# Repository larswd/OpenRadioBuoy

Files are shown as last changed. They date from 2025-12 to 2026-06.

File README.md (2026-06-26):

# The Open Radio Buoy (ORB)
This repository contains the firmware, list of hardware and PCB schematics that collectively make up the Open Radio Buoy (ORB), as described in our paper which you can read [here](https://arxiv.org/abs/2601.05615). The buoy is designed to be a low-cost, open-source drifter for coastal water measurements. The archive is currently incomplete, but more updates will come. 

## List of hardware components

### Drifter

A single ORB drifter's electronics is made up of the following components, with links to manufacturer website. 

| Quantity | Component | Note |
| -------- | --------- | ---- |
| 1 | [Seeed Studio Wio-E5 mini](https://wiki.seeedstudio.com/LoRa_E5_mini/) | Comes with actory protection which needs to be disabled manually |
| 1 | [Adafruit Ultimate GPS](https://www.adafruit.com/product/746)          | Comes with a holder for a CR1220 clock battery to remember last fix.| 
| 1 | [Adafruit SD Breakout](https://www.adafruit.com/product/254)           | | 
| 1 | [DS18B20 temperature sensor](https://www.sparkfun.com/temperature-sensor-waterproof-ds18b20.html) | |
| 1 | [Pololu 3.3 V Step up/Step down voltage regulator](https://www.pololu.com/product/2122) | |
| 1 | 10 kOhm resistor  |
| 1 | 4.7 kOhm resistor  |
| 2 | 33.0 Ohm resistors |
| 1 | Magnetic switch         | Normally open is *strongly* recommended. Not mandatory. |
| 1 | [CAB-14574 connector](https://no.mouser.com/ProductDetail/474-CAB-14574) | Not mandatory, but makes arming and disarming the drifter easier |
| 1 | Strong magnet | To turn off the buoy from outside the buoy container | Not mandatory |

As for battery power, the buoy works with any kind of power source with a voltage between 2.7 and 11.8 V, as per the Pololu documentation. This can be either a Lithium battery such as [Saft LSH20](https://www.nkon.nl/novat/saft-lsh-20-lithium-battery-3-6v.html), although any user should be aware of the [risks of using Lithium powered batteries](https://www.relionbattery.com/blog/the-truth-about-lithium-batteries-and-safety). Alternatively, several alkaline batteries (as was done by the [SFY](https://github.com/gauteh/sfy)) in series can be utilised without need of modifying the circuit. 

### Base station

A single ORB base station electronics is made up of the following components, with links to manufacturer website. 

| Quantity | Component | Note |
| -------- | --------- | ---- |
| 1 | [Seeed Studio Wio-E5 mini](https://wiki.seeedstudio.com/LoRa_E5_mini/) | Comes with actory protection which needs to be disabled manually |
| 1 | [Adafruit SD Breakout](https://www.adafruit.com/product/254)           | Not mandatory |
| 1 | [Pololu 5 V Step up/Step down voltage regulator](https://www.pololu.com/product/4082) | |
| 1 | [CAB-14574 connector](https://no.mouser.com/ProductDetail/474-CAB-14574) | Not mandatory, but makes arming and disarming the drifter easier |
| 1 | [Blues Notecard Cellular](https://shop.blues.com/collections/notecard/products/notecard-cellular?variant=44541263118577) | Check the coverage diagram for your area before ordering |
| 1 | [Blues Notecarrier A](https://shop.blues.com/products/carr-al) | |
| 1-2 | Capacitor (One [1F](https://no.mouser.com/ProductDetail/Eaton-Electronics/KVR-5R0V105-R?qs=4ASt3YYao0XQhknEZPCgzw%3D%3D) or two [10F](https://no.mouser.com/ProductDetail/Knowles-Illinois-Capacitor/DGH106Q2R7C?qs=vmHwEFxEFR9tIw5tsmf9eg%3D%3D)) | Capacitor strength dependent on power source |

If you choose to power the base station with Lithium batteries like the aforementioned LSH20, then a single 1 F capacitor is sufficient to keep the base station operational. If, however, you use alkaline batteries as your power source then 10 F capacitors are required to ensure that the high energy spikes drawn by the GSM module can be met. 

### Other components
To code the WiO E5 mini, remember to order at least one [ST link](https://www.adafruit.com/product/2548) and some [Female-Male jumper cables](https://no.rs-online.com/web/p/breadboard-jumper-wires/2048242) in order to be able to upload the software to the buoys and base stations. 

## Assembly instructions

### Electronics assembly - Buoys
Order the [PCBs](https://github.com/larswd/OpenRadioBuoy/tree/main/hardware/buoy_PCB) by uploading the Gerber files folder to your favourite PCB manufacturer, such as [JLCPCB](https://cart.jlcpcb.com/quote?spm=jlcpcb.Public.2006) or [Seeed studio](https://www.seeedstudio.com/fusion_pcb.html). Then order the components listed above according to how many buoys you plan to make. They can be ordered either from the manufacturer, and in many cases from a local electronics distributor. 

The assembly can begin once you have all the components at hand. The PCBs offered are currently Through-Hole PCBs, and requires therefore manual soldering. As both sides of the PCB is utilized in somewhat overlapping segments, it is vital that some components are soldered before others. I would recommend soldering in this order: 

1. Wires to the power pins at the bottom of the PCB
2. Pololu
3. Trim the pins on the back of the Pololu, then tape. 
4. SD card writer
5. Trim the pins on the back of the SD card writer, then tape.
6. GPS
7. Trim GPS pins
8. Wio E5 mini
9. MF pin sockets for the programmable pins
10. DS18B20
11. Resistors
12. Magnetic switch
13. Battery connectors
    
### Electronics assembly - Base stations
Order the [PCBs](https://github.com/larswd/OpenRadioBuoy/tree/main/hardware/BST_PCB) by uploading the Gerber files folder to your favourite PCB manufacturer, such as [JLCPCB](https://cart.jlcpcb.com/quote?spm=jlcpcb.Public.2006) or [Seeed studio](https://www.seeedstudio.com/fusion_pcb.html). Then order components according to the amount of base stations you plan on creating. 
The assembly can begin once you have all the components at hand. The PCBs offered are currently Through-Hole PCBs, and requires therefore manual soldering. Unlike the buoy PCBs, there is little overlap between components and they can be soldered on in pretty much any order. Some things to keep in mind

1. The power regulator will somewhat block easy access to the USB port on the LoRa module. Hence, it is strongly recommended to not solder the module directly onto the board. Instead, we recommend soldering on a 1x5 2.54 mm MF pin header, as the power regulator then easily can be removed and reattached if you need to upload software updates. 
2. Super capacitors have a polarity, indicated by the arrows on both the PCB and often on the capacitors themselves. Please check the data sheet of your capacitor before soldering. 
3. The Notecard might need to be initialized before use. A handy guide can be found [here](https://dev.blues.io/quickstart/notecard-quickstart/notecard-and-notecarrier-a/).
4. The notecard sends the data to Blues' Notehub, which is project based. By default, the ORB base station is set to send the data to a notehub project owned by us. We are willing to share any data we receive as well as the url to our dashboard, but if you want to administrate your data yourself, and who gets access to it, then you can create your own project at [https://notehub.io/projects], then you simply exchange the notehub project url at (currently) line 14 in [the GSM module header](https://github.com/larswd/OpenRadioBuoy/tree/main/firmware/common_libraries/gsm/src/gsm.h) with your new project url (which should look something like ```me.proton.larswd:my_cool_project```)

### Installation instructions - Buoy
The installation of the ORB firmware is a two-step process. First, you need to remove the write protection that the WiO-E5-mini comes with out of the box. To do so, you first need a USB C cable and a [ST-Link](https://www.adafruit.com/product/2548). Then, download the [STM32CubeProgrammer](https://www.st.com/en/development-tools/stm32cubeprog.html#get-software), and install it. Once it is installed, connect the Wio-E5 mini to your laptop via both the USB C cable and with the ST-link. Here, you need to connect the right pins, and we list them as (ST Link pin/Wio pin), 
- (RST/RST),
- (SWCLK/CLK),
- (SWDIO/DIO),
- (GND/GND).
Afterwards, set ```shared``` to ```Enabled``` and ```Reset mode``` to ```Hardware reset```. If you press the circular arrows button, then if everything works you should see under the **OB** header an option called **Read out protection**, set this drop-down menu to AA and press **Apply**. The buoy is now programmable! See a helpful visual guide below: 

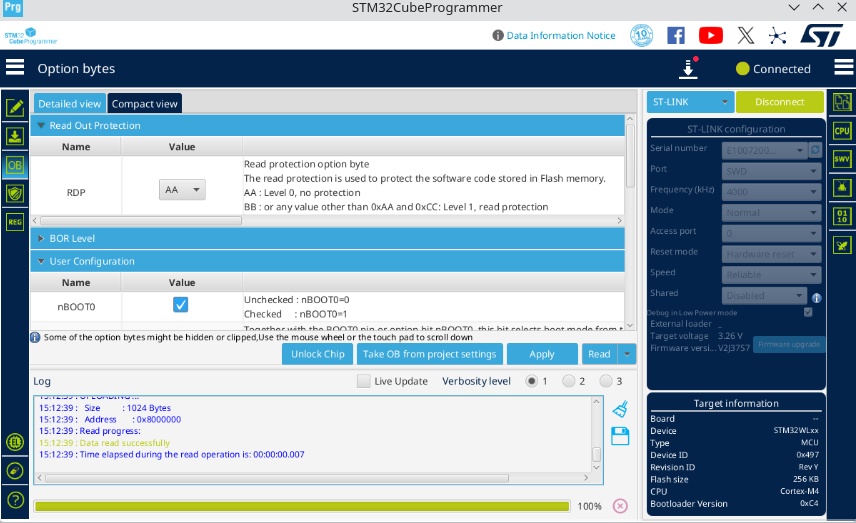
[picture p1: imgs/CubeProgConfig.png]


The next step is to upload the firmware. If you are happy with the default configuration, then you can jump to the next paragraph. Otherwise, you can configure most important parameters in the [configuration file](firmware/drifter/src/config.h). What each parameter does is described in the [drifter README file](firmware/drifter/README.md).

Once you have a configuration file you are satisfied with, you can upload the firmware to the buoy. To do so, we use [PlatformIO IDE for vscode](https://docs.platformio.org/en/latest/integration/ide/vscode.html), an extension for visual studio code made for programming microcontrollers. Once you have installed platformIO, click **Open project** under the **PIO Home** tab, and navigate to the *firmware/drifter* folder and click **Open drifter**. From here, platformio will open and read the necessary configurations. Once the project has finished loading, which you can see when several new buttons have appeared at the bottom taskbar in visual studio code, then you can upload the code. An image of a fully loaded platformio instance is shown below, in particular note the checkmark and arrow key at the very bottom. 
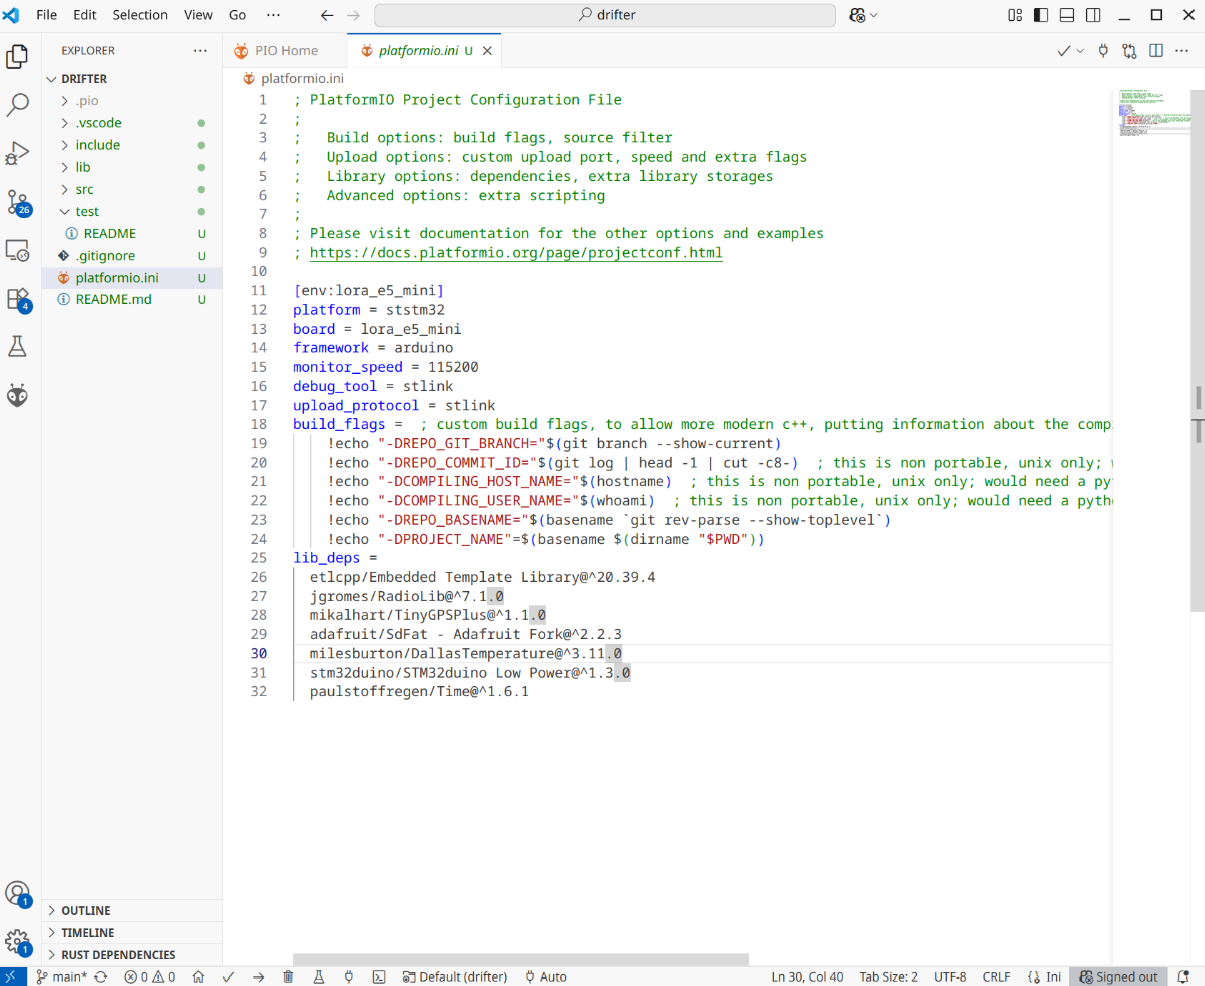
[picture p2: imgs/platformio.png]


To upload the code, connect the ORB to your computer both with the ST link (connection instructions are given above) and the USB C cable, then press the upload button (The arrow icon), then wait until the terminal that popped up states something close to 
```
============================================= [SUCCESS] Took 3.12 seconds =============================================
```
### Installation instructions - Base station
The steps for installing the firmware to the base station is more or less the same as the buoy one, with the exception that you instead open the **basestation** project rather than the **drifter** project. Furthermore, you should here remember to go into the ```config.h``` file and set a unique base station ID. See the line where it says:
static constexpr uint8_t base_station_ID            {x};```
Where ```x``` is some number. Set ```x``` to any whole number between 0 and 255 that you have not previously used in your base station fleet, then upload the code to the base station. **REMEMBER**: See bullet point 4 of the assembly instructions for the base station regarding data management. 

### Final assembly 

The container components we used are given in the table below 

| Component | Role |
| --------- | ---- |
| [Pipe connector](https://www.biltema.no/bygg/vvs/sanitet-og-vann/avlop/innendors-avlop-gra/innendors-avlop-gra-75-mm/avlopsror-skjotemuffe-75-mm-2000059003) | Main electrical component housing |
| [Lid 75 mm](https://www.biltema.no/bygg/vvs/sanitet-og-vann/avlop/innendors-avlop-gra/innendors-avlop-gra-75-mm/avlopsror-endestopp-75-mm-2000059011) | Top lid |
| [Reduction 75->50mm](https://www.biltema.no/bygg/vvs/sanitet-og-vann/avlop/innendors-avlop-gra/innendors-avlop-gra-75-mm/avlopsror-reduksjon-o-7550-mm-2000065100) | Ballast and battery container |
|[Lid 50 mm](https://www.biltema.no/bygg/vvs/sanitet-og-vann/avlop/innendors-avlop-gra/innendors-avlop-gra-50-mm/avlopsror-endestopp-o-50-mm-2000065102) | Bottom lid |
| [Large cable gland](https://no.rs-online.com/web/p/cable-glands/6694673) | Cable gland for the antenna |
| [Small cable gland](https://no.rs-online.com/web/p/cable-glands/6694660) | Cable gland for DS18B20 |
| [Ballast](https://www.frederiksen-scientific.no/produkt/lodd-med-krok-200-g/191002) | We use 300 grams of tin ballast in each ORB drifter |
| [XPS 300](https://thaugland.no/butikk/byggevarer/isolasjon/mark-grunn-isolasjon/xps/jackon-isolasjon-xps-20mm-300-jackofoam/) | 20 mm isolation foam as a flotation device around the top for increased stability. |

To assemble, drill two holes in the top lid for the two cable glands. Thereafter, sand the lid to ensure that the top is as uniform as possible. Apply generously with grease on each of the rubber bands on the cable glands and inside the pipes. Insert the fully assembled ORB electronics through the cable glands in the lid. Tighten the antenna gland, but not the thermistor gland, and watch carefully to ensure that the tightening does not loosen the antenna connection to the main circuit board. Insert the bottom lid into the reduction, then place the ballast in the bottom 50 mm diameter pipe, use silicone or other lipophile glue to ensure that it stays put, and add a small cardboard or plastic disc at the top to ensure an even surface. Mark where the magnetic switch is supposed to be placed on the pipe connector with permanent marker, then tape the switch on the other side underneath the marker. Be careful, as improper switch placement means that it is difficult to check if the buoy is turned off while inactive. Cut out a small square or disk of the XPS 300, approximately 15 cm wide at the widest, and cut a 75 mm diameter hole in the middle. Insert the lid into the XPS 300, and then into the pipe connector. Connect the battery to the electronics, and validate that the switch works as intended. Finally, insert the reduction into the connector, and seal the buoy by tightening the thermistor cable gland. 


Your ORB drifter is now ready to use. 

### Final assembly - Base station

As the base stations will, most likely, not be floating in water directly, there is significantly more leeway in container design. Pick any waterproof container large enough, and drill a single hole large enough for the [cable gland](https://no.rs-online.com/web/p/cable-glands/6694673). In our deployments, we used this [fishing box](https://www.clasohlson.com/no/Vanntett-boks-/p/31-8544) which could fit three D Cell batteries and the base station, although it was a bit too cramped. Hence, we recommend finding a slightly larger container if possible. 

## Images and deployments
Images from the deployments will come soon. 

## A small thanks 
We would also like to thank the authors of the many open source libraries that collectively form the code base of the Open Radio Buoy. In no particular order, we wish to express our gratitude to 
- [Paul Stoffregen and contributors' OneWire](https://github.com/PaulStoffregen/OneWire)
- [Mikal Hart and contributors' TinyGPSplus](https://github.com/mikalhart/TinyGPSPlus)
- [Jan Gromeš and contributors's Radiolib](https://github.com/jgromes/RadioLib)
- [Bill Greiman's SdFat](https://github.com/greiman/SdFat)
- [Jean Rabault's OpenMetBuoy](https://github.com/jerabaul29/OpenMetBuoy-v2021a)

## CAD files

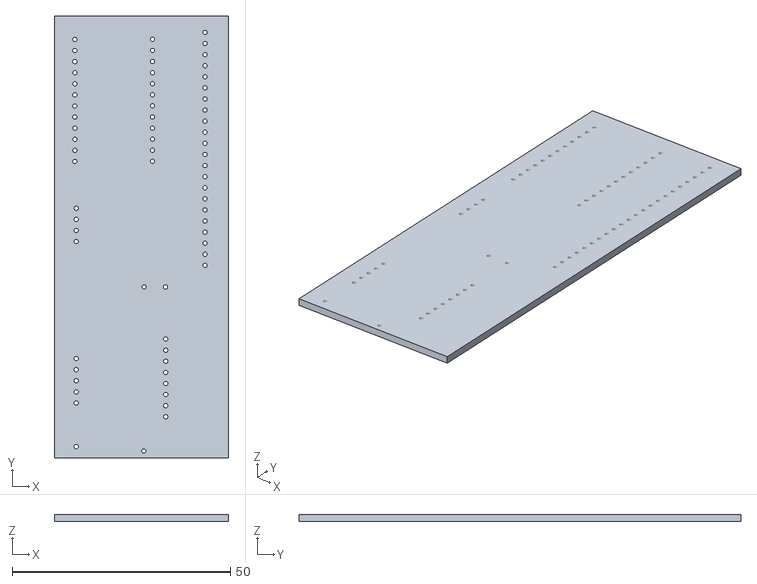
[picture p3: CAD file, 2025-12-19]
hardware/BST_PCB/BST_BCP.stl
39.9 x 101.2 x 1.60

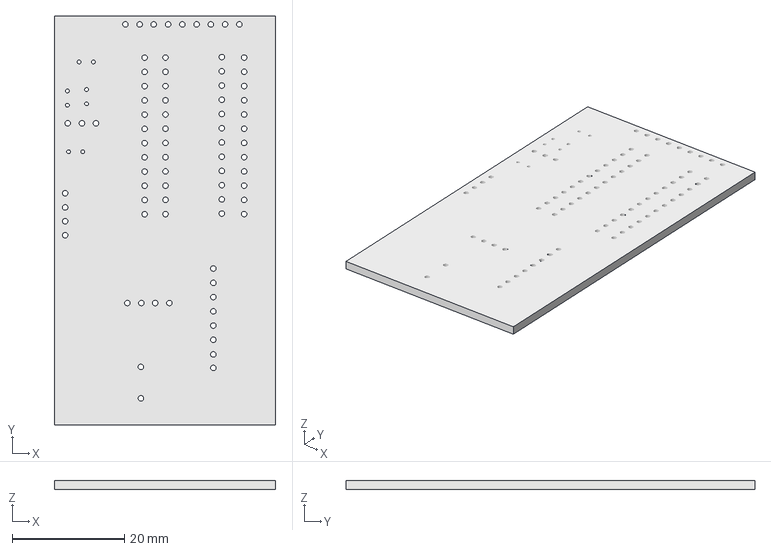
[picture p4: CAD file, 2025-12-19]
hardware/buoy_PCB/PCB_FCAD.FCStd
39.5 x 73.0 x 1.60 mm
Pcb_11bb
Pcb_11bb (Meshed)

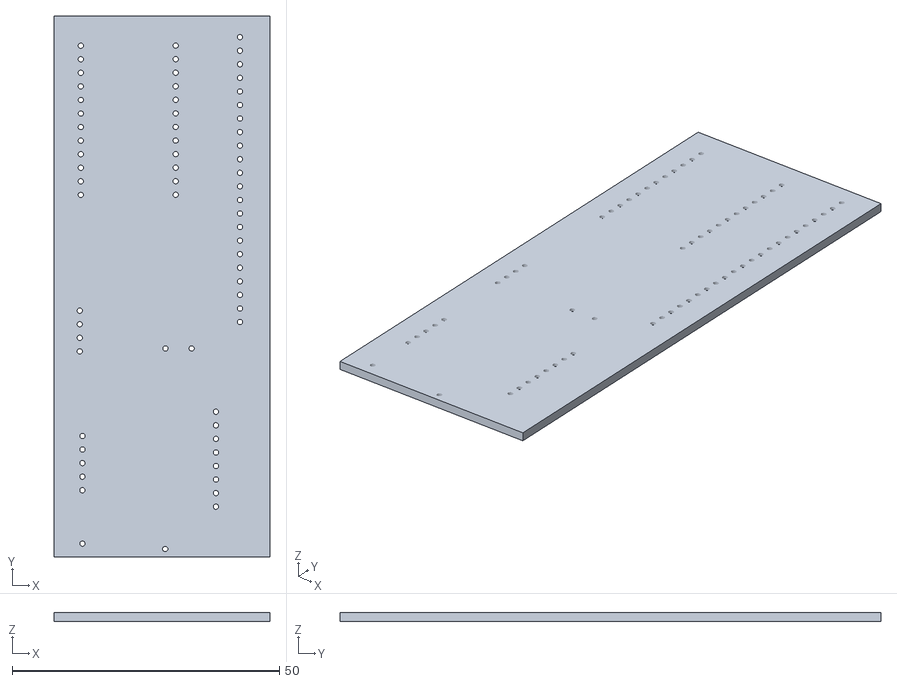
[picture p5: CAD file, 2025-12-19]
hardware/BST_PCB/BST_BCP_v2.stl
40.4 x 101.3 x 1.60

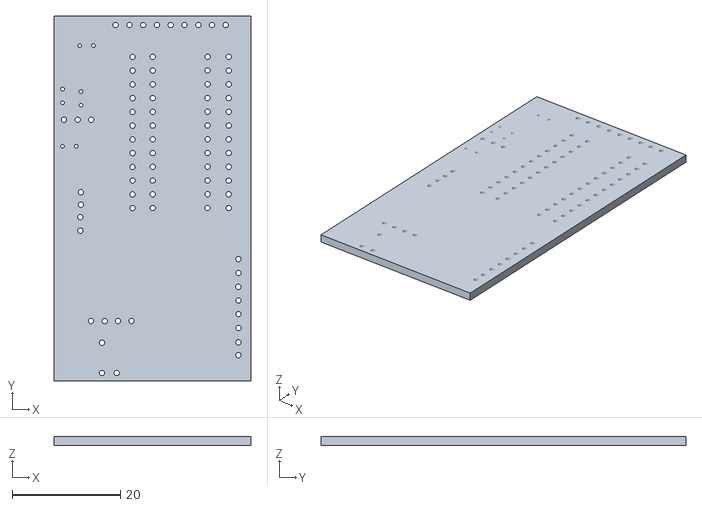
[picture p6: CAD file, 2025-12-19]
hardware/buoy_PCB/PCB_meshed.stl
36.4 x 67.4 x 1.60

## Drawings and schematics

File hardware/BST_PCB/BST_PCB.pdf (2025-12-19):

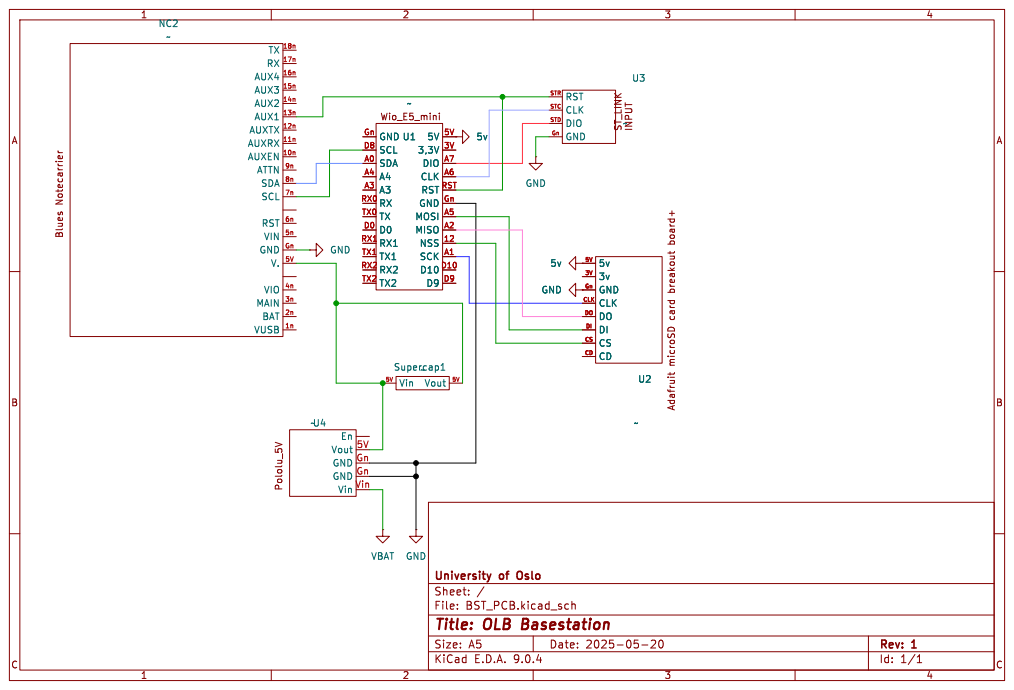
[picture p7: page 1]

Id: 1/1 Title: OLB Basestation

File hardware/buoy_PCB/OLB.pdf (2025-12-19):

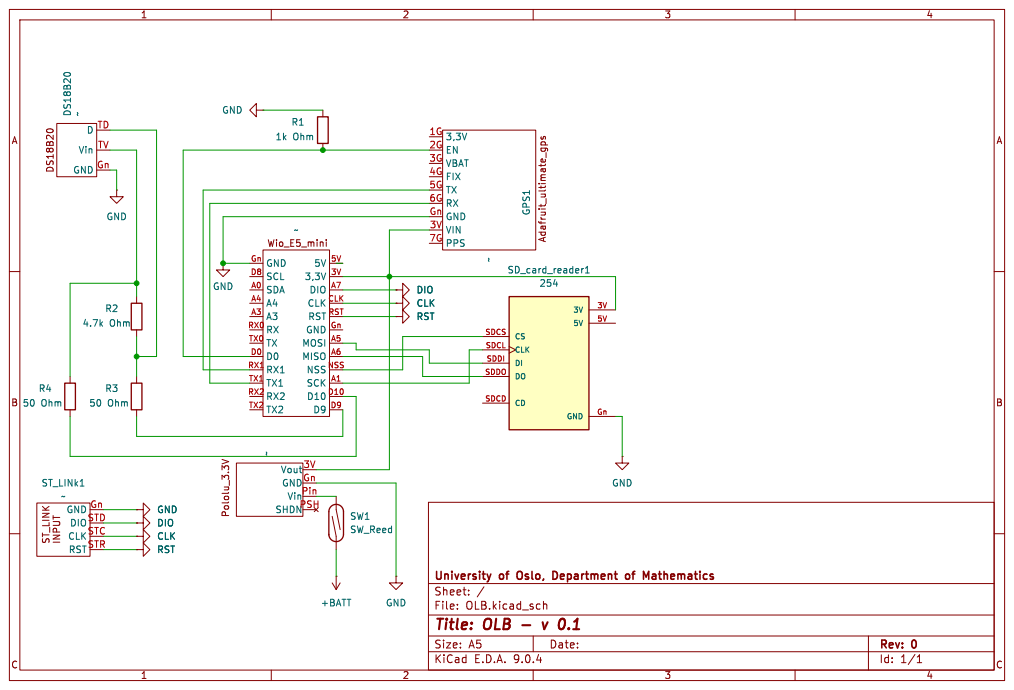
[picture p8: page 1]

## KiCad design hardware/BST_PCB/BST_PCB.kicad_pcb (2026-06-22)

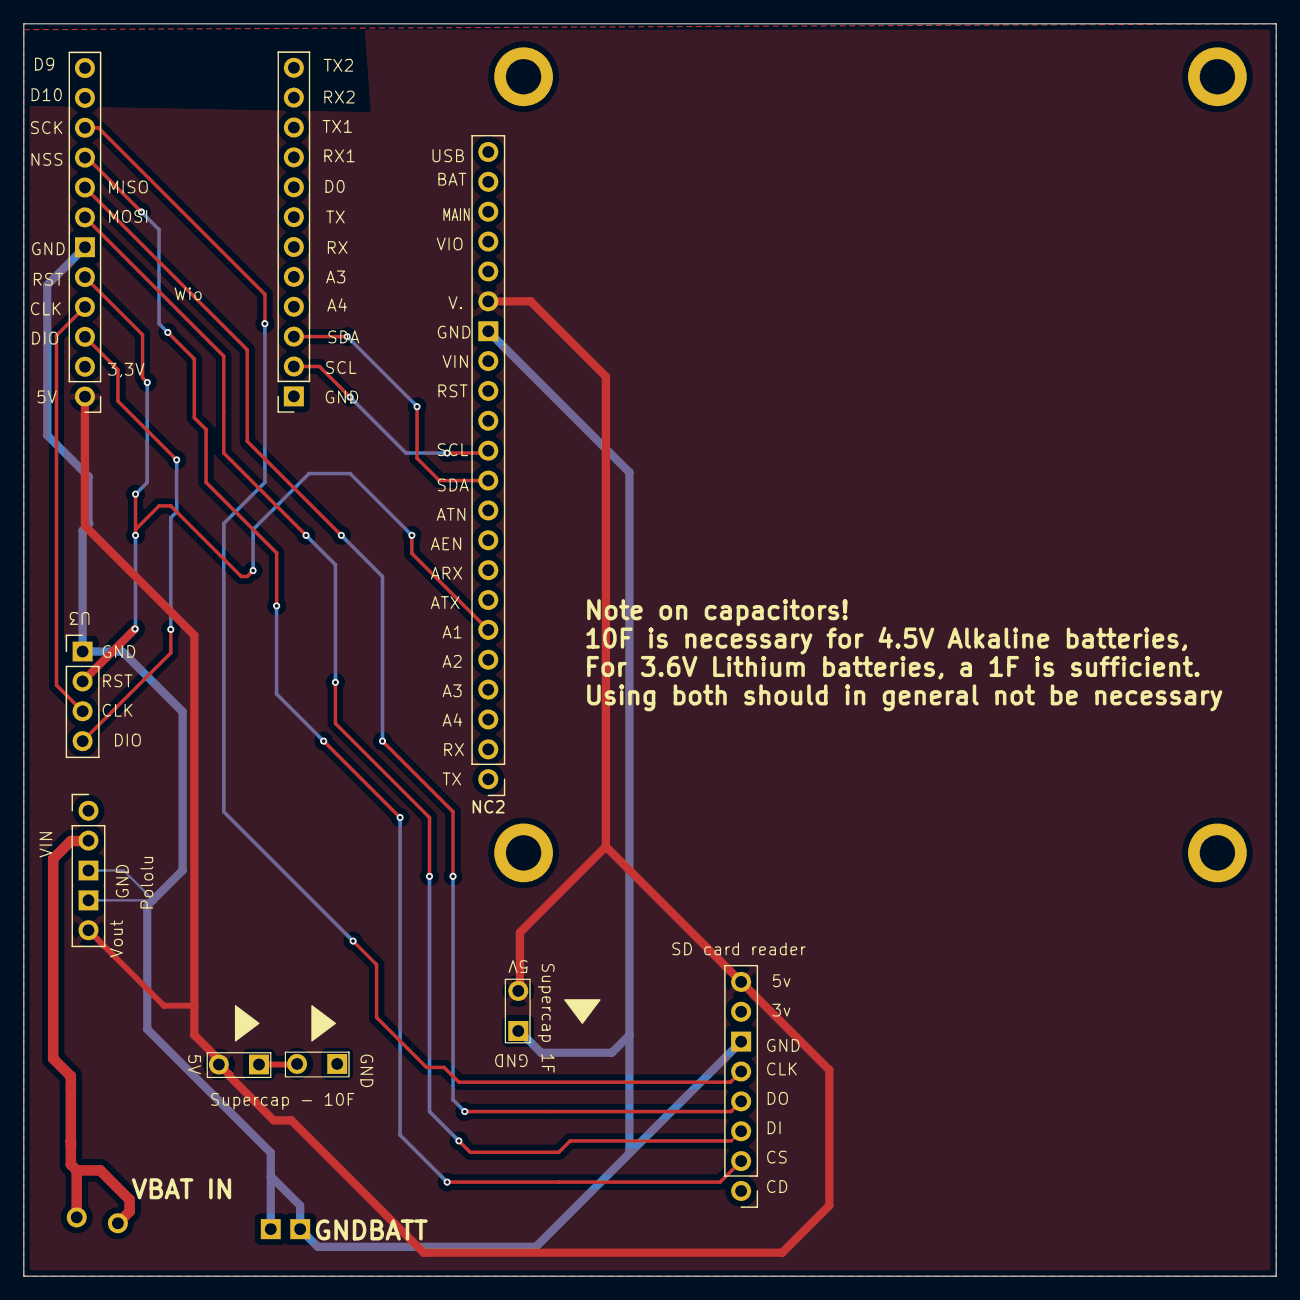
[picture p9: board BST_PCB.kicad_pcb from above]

Board: 2 copper layers, 106.5 x 106.5 mm, 8 parts (0 on the bottom side), 11 nets.

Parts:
NC2: notecard
Pololu: Pololu5v
SD card reader: SDReader
Supercap2: Supercap
Supercap 1F: Supercap
Supercap - 10F: Supercap
U3: STLINK
Wio: Wio E5 mini

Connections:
5v: NC2.5v, Pololu.Vout (Vin), SD card reader.5v, Supercap2.5V (5v), Supercap 1F.5V (5v), Wio.5V
GND: NC2.Gn (GND), Pololu.GND, Pololu.Gn (GND), SD card reader.Gn (GND), Supercap 1F.vout (GND), Supercap - 10F.vout (GND), U3.Gn (GND), Wio.Gn (GND)
unnamed: NC2.13n (AUX1), U3.RST, Wio.RST
unnamed: NC2.7n (SCL), Wio.D8 (SCL)
unnamed: NC2.8n (SDA), Wio.A0 (SDA)
unnamed: U3.CLK, Wio.CLK
unnamed: U3.DIO, Wio.A7 (DIO)
unnamed: SD card reader.DO, Wio.A6 (CLK)
unnamed: SD card reader.DI, Wio.A5 (MOSI)
unnamed: SD card reader.CS, Wio.NSS
unnamed: SD card reader.CLK, Wio.A1 (SCK)

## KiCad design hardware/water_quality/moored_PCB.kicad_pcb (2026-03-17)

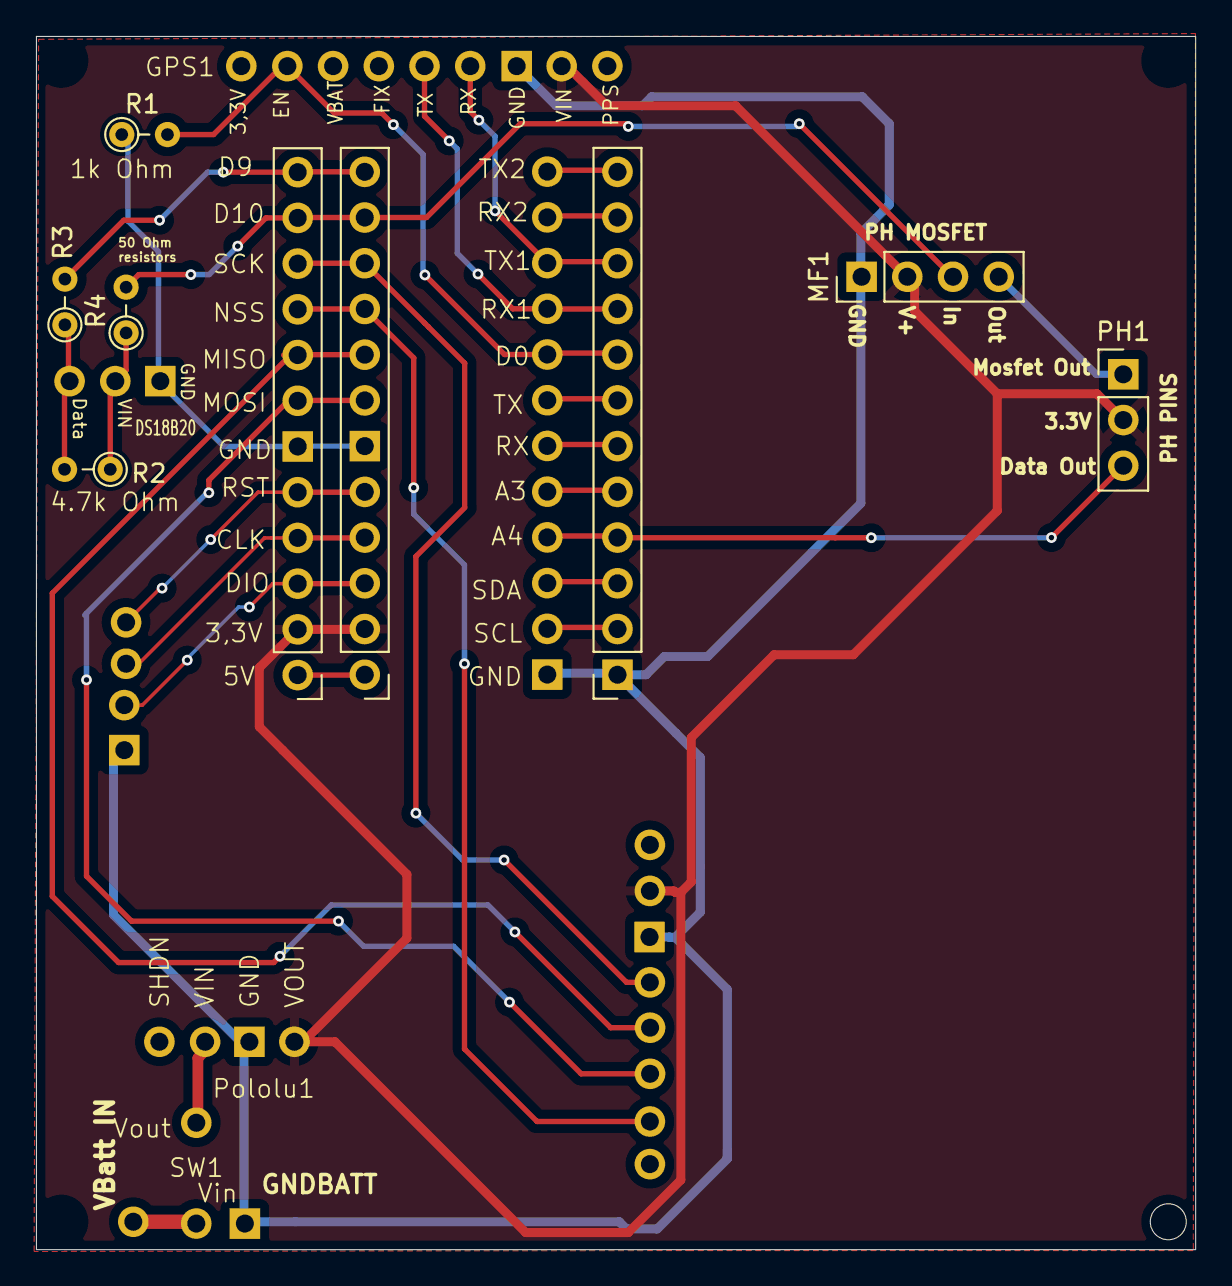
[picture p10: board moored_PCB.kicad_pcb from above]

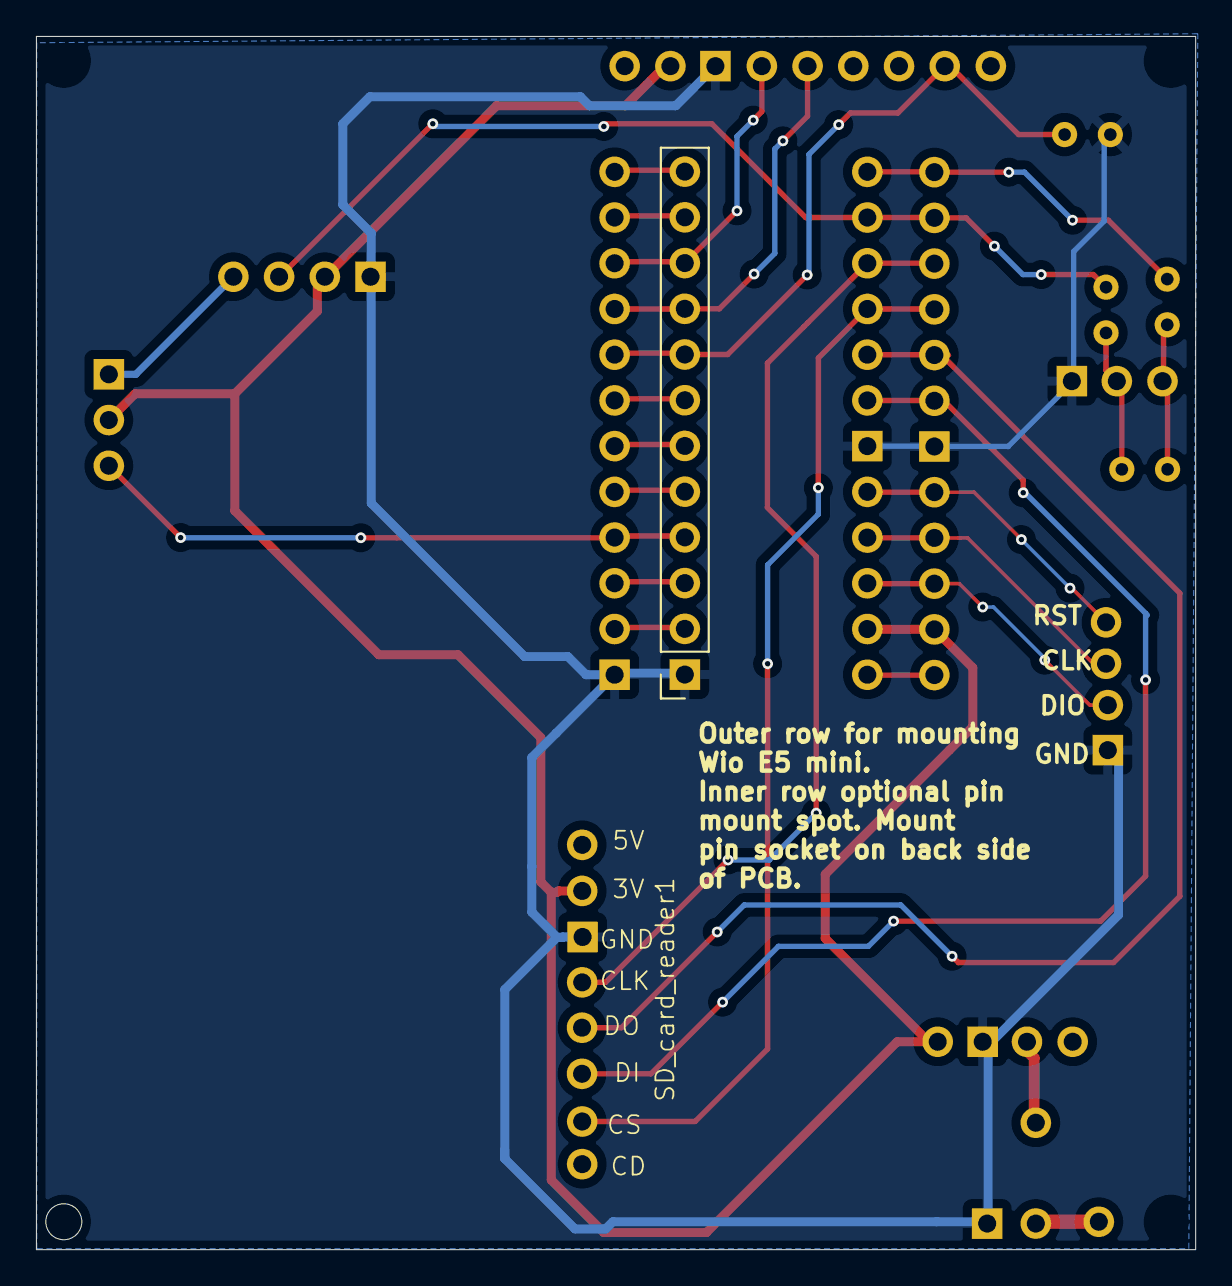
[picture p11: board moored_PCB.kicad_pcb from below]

Board: 2 copper layers, 64.4 x 67.4 mm, 13 parts (2 on the bottom side), 14 nets.

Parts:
DS18B20: DS18B20
GPS1: GPS
MF1: PinHeader_1x04_P2.54mm_Vertical
PH1: PinHeader_1x03_P2.54mm_Vertical
Pololu1: Pololu3,3V
R1: 1k Ohm; R_Axial_DIN0204_L3.6mm_D1.6mm_P2.54mm_Vertical
R2: 4.7k Ohm; R_Axial_DIN0204_L3.6mm_D1.6mm_P2.54mm_Vertical
R3, R4: 50 Ohm; R_Axial_DIN0204_L3.6mm_D1.6mm_P2.54mm_Vertical
RHS Wio pins: PinSocket_1x12_P2.54mm_Vertical
SD_card_reader1: 254; SD_writer
SW1: SW_Reed; ReedSwitch
Wio1: WIO_E5_THT

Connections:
3V: GPS1.3V (VIN), MF1.2, PH1.2, Pololu1.3V (Vout), SD_card_reader1.3V, Wio1.3V (3,3V)
GND: DS18B20.Gn (GND), GPS1.Gn (GND), MF1.1, Pololu1.Gn (GND), R1.1, RHS Wio pins.1, SD_card_reader1.Gn (GND), Wio1.Gn (GND)
MISO: SD_card_reader1.SDDO (DO), Wio1.A6 (MISO)
MOSI: SD_card_reader1.SDDI (DI), Wio1.A5 (MOSI)
NSS: SD_card_reader1.SDCS (CS), Wio1.NSS
unnamed: DS18B20.TD (D), R2.2, R3.1
unnamed: DS18B20.TV (Vin), R2.1, R4.1
unnamed: GPS1.2G (EN), R1.2, RHS Wio pins.8, Wio1.D0
unnamed: GPS1.6G (RX), RHS Wio pins.10, Wio1.TX1
unnamed: GPS1.5G (TX), RHS Wio pins.9, Wio1.RX1
unnamed: Pololu1.Pin (Vin), SW1.1
unnamed: R3.2, Wio1.D9
unnamed: MF1.3, R4.2, Wio1.D10
SCK: SD_card_reader1.SDCL (CLK), Wio1.A1 (SCK)

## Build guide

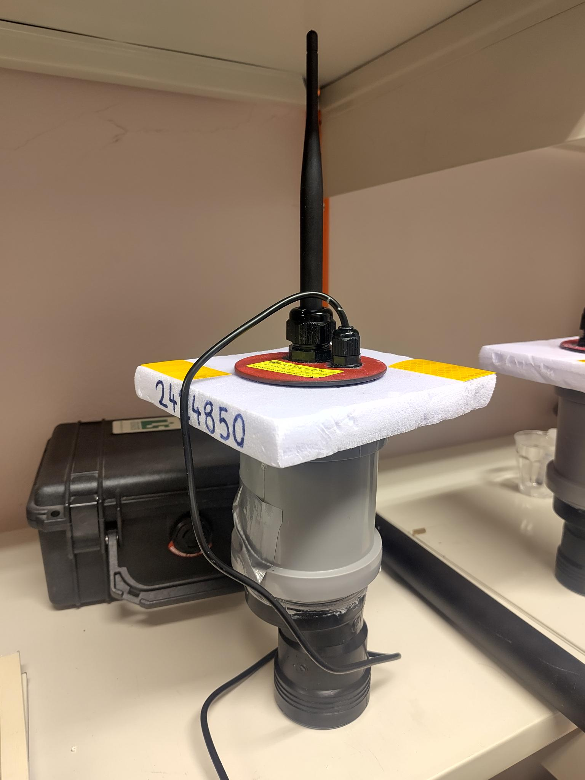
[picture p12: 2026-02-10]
imgs/assembled_OLB.png

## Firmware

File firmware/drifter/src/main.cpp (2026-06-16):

#include <Arduino.h>
#include "config.h"
#include "etl_error_manager.h"
#include "messages.h"
#include "lora_transceiver.h"
#include "gps_manager.h"
#include "sd_writer.h"
#include "thermo_manager.h"
#include "IWatchdog.h"
#include "STM32LowPower.h"
#include "TimeLib.h"
/*
  TODO: 
  Get a good algorithm for getting a date stamp from GPS.
  This feature is currently disabled. 
*/


/* Workaround for millis not increasing during sleep cycles */
uint32_t measurement_timer;
uint32_t beacon_timer = 0;
static uint32_t sleep_cycles_measurement  = 0;
static uint32_t sleep_cycles_transmission = 0;
static uint32_t sleep_cycles_beacon       = 0;
static uint32_t iterations_counter = 0;


uint32_t millis_time_corrected(uint32_t sleep_cycles){
  return millis() + sleep_cycles*sleep_time;
}

void setup() {

  // Serial debugging can be turned on or off with the debug_serial flag
  if (debug_serial){
    Serial.begin(serial_baud);
    Serial.println("Serial initialized!");
    delay(100);
  }

  // We try to enable rtc timing
  setSyncInterval(1);

  // Watchdog begin
  if (enable_watchdog){
    IWatchdog.begin(1000*watchdog_wait_time);
  }
  /*
    Note, watchdog has .isReset member which allows us to resume operations in case of 
    shutdown. Look into implementation of restore from SD/RAM
  */

  // Start SD
  bool SD_fail = sd_writer.begin();  
  int8_t status = sd_writer.startLogging("boot_info.txt");
  if (!SD_fail && debug_serial){
    Serial.println("SD opened");
    Serial.print("Status code: ");
    Serial.println(status);
  }
  IWatchdog.reload();


  /*
    Buoy will not start without working radio.
  */
  LORA.beginRadio(LoRa_freq_receive, LoRa_bw, LoRa_sf, LoRa_cr, LoRa_power);
  LORA.getWiOID();
  if (LORA.state == RADIOLIB_ERR_NONE){
    sd_writer.logString("Radio functional");
  } else {
    sd_writer.logString("Radio failed to start. Freezing sensor.");
    while(1);
  }

  if (SD_fail){
    if (debug_serial){
      Serial.println(F("SD card mount failed. Proceeding with Radio only"));
    }
    delay(100);
  }
  
  /*
    We monitor possible overflow in ETL storage containers
  */
  etl::error_handler::set_callback<etl_error_func>();

  sd_writer.logString("Beginning GPS");

  IWatchdog.reload();
  gps_manager.begin(GPS_baud);

  int8_t  nofix = 1;

  /*
    Buoy will not advance until it has gotten a fix
  */
  while (nofix){
    gps_manager.updateTimestamp(10*max_GPS_read_time, true);
    nofix = gps_manager.performNReadings(1,10*max_GPS_read_time, true);
    delay(100);
    IWatchdog.reload();
  }

  gps_manager.processReadings(false);

  /*
    We need to read the attached thermistors for a buoy ID
  */
  thermo_manager.begin(PA9,PB10);

  gps_manager.getDeploymentMessage(LORA.WiO_ID);
  LORA.startup_timestamp = gps_manager.timestamp;
  IWatchdog.reload();
  if (debug_serial){
    Serial.println("Sending deployment message");
  }
  if (IWatchdog.isReset() == false && transmitDeploymentMessage){
    /*
      We wait until we get a fix from a base station before proceeding.
      Allows us to make sure the buoy works before tossing it into the water. 
    */
    while (!LORA.connectToBaseStation(max_radio_fix_look_time, max_radio_fix_look_time)) {
      IWatchdog.reload();
    }
    
    LORA.transmitB(gps_manager.deploymentMessage, deployment_message_size);
    sd_writer.logString(gps_manager.deploymentMessage, deployment_message_size);
    LORA.waitUntilReady();
  }
  
  LORA.lastTransmission = millis();
  if (IWatchdog.isReset() == true){
    //We check to see if the buoy crashed
    sd_writer.logString("Watchdog crashed during execution of loop. This is a reboot.");
  }


  measurement_timer = millis();
  if (enable_recovery_beacon){
    beacon_timer = millis();
  }
  /*
    Start low power management. As low power requires all connections 
    to be off, we turn them off here, before
    enabling them again in the loop. 
  */ 
  LowPower.begin();
  gps_manager.shutdownGPS();
  sd_writer.closeLog();
  thermo_manager.sleep();
  if (debug_LED_enabled){
    digitalWrite(LED_BUILTIN, LOW);
  }
  LORA.sleep();

  
  // We try to recover a GPS measurement:
  //char targetFile[64];
  //sprintf(targetFile, "readings/reading%05d.txt", 3);
  //sd_writer.startReading(targetFile);
  //sd_writer.readFile();
  //gps_manager.getMeasurementFromFile();
  //thermo_manager.getMeasurementFromFile();
  //sd_writer.closeRead();


  if (debug_serial){
    Serial.println("Setup complete, loop beginning");
    delay(100);
    Serial.end();
  }


}

void task_measure_gps_temp() {

  // Measure time!
  unsigned long measurement_start = millis();

  if (debug_LED_enabled){
    digitalWrite(LED_BUILTIN, HIGH);
  }

  // Wake up sensors
  gps_manager.begin(GPS_baud);
  thermo_manager.wake();
  IWatchdog.reload();

  char logname[25];
  sprintf(logname, "readings/reading%05d.txt", sd_writer.logCount);
  
  if (!sd_writer.active){
    sd_writer.begin();
  }
  sd_writer.startLogging(logname);
  IWatchdog.reload();

  // We read each sensor
  if (debug_serial){
    Serial.println("Reading sensors");
    Serial.println(gps_manager.iterations);
    delay(100);
  }
  
  // success_gps_read is 0 if the buoy got a fix
  uint8_t success_gps_read = gps_manager.updateTimestamp(max_GPS_read_time, resync_RTC_using_GPS);
  if (success_gps_read == 0){
    gps_manager.performNReadings(readings_per_measurement,max_GPS_read_time, log_every_reading);
    gps_manager.processReadings(true);

    // We should turn off the GPS post reading due to power consumption
    gps_manager.shutdownGPS();

    thermo_manager.takeReadings(max_sensor_read_time, gps_manager.timestamp, log_every_reading);
    thermo_manager.processReadings();


    IWatchdog.reload();
    // We update the measurements period to reflect the new motion paradigme
    if (enable_motion_detection){
      LORA.updateMeasurementFrequency(gps_manager.current_buoy_velocity, maximal_measurement_period, minimal_measurement_period);
    }
  } else {
    // If no fix was found, we skip this measurement and hope for better luck the next time around. 
    gps_manager.shutdownGPS();
  }
  // Turning off remaining sensors
  sleep_cycles_measurement = 0;
  measurement_timer = millis_time_corrected(sleep_cycles_measurement);
  thermo_manager.sleep();
  sd_writer.closeLog();
  IWatchdog.reload();

  // Turn off LED
  if (debug_LED_enabled){
    digitalWrite(LED_BUILTIN, LOW);
  }

}
  

void task_transmit() {

  if (debug_serial){
    Serial.println("Looking for base station");
  }

  if (debug_LED_enabled){
    for (int i = 0; i < 3; i++){
      digitalWrite(LED_BUILTIN, LOW);
      delay(800);
      digitalWrite(LED_BUILTIN, HIGH);
      IWatchdog.reload();
    }
    digitalWrite(LED_BUILTIN, LOW);
  }
  
  char logname[30];
  sprintf(logname, "messages/transmission%05d.txt", LORA.msgCounter);

  if (!sd_writer.active){
    sd_writer.begin();
  }

  sd_writer.startLogging(logname);
  IWatchdog.reload();
  LORA.wakeUp();
  sd_writer.logString("Looking for base station");

  // Handshake
  if (perform_handshake){
    if (LORA.connectToBaseStation(max_radio_fix_look_time, max_radio_wait_time)){
    sd_writer.logString("Hands shaked");
    } else {
    sd_writer.logString("No base station found");
    } 
    delay(send_delay_after_handshake);
  } else {
      // We do not check if a base station is present
      LORA.available = true;
      LORA.listenTime = 60*s_2_ms;
  }

  Message_Data message_data;
  sd_writer.logString("Transmitting data\n--------\n");

  // We dump as much information as possible to the base station
  // In the time period alloted to us
  while (LORA.available && (thermo_manager.temperatures.size() > 0)){

    // GPS data
    if (debug_serial){
        Serial.print("Sending G: "); Serial.print(GPS_message_size); Serial.println(" bytes");
    }
    
    gps_manager.updateTransmitMessage();
    message_data = LORA.sendData(gps_manager.msgB, GPS_message_size, 10000);
    delay(500);

    sd_writer.logByteArray(gps_manager.msgB, GPS_message_size);
    sd_writer.logSignalInfo(message_data.RSSI, message_data.SNR);

    // Thermometer data
    if (debug_serial){ Serial.print("Sending T: "); Serial.print(thermo_message_size); Serial.println(" bytes");}

    thermo_manager.updateTransmitMessage();
    message_data = LORA.sendData(thermo_manager.msgB, thermo_message_size, 10000);
    IWatchdog.reload();

    delay(500);
    sd_writer.logByteArray(thermo_manager.msgB, thermo_message_size);
    sd_writer.logSignalInfo(message_data.RSSI, message_data.SNR);

    delay(200);
    LORA.packet_count++;
    IWatchdog.reload();

    if (debug_serial){
      Serial.print("Available: ");
      Serial.println(LORA.available);
      Serial.print("Num packets left: ");
      Serial.println(thermo_manager.temperatures.size());
    }

    delay(500);
  }
  
  // Wrap up transmission, wait for base station instructions
  if (LORA.available){
    LORA.transmitFinished(thermo_manager.temperatures.size());
    if (enable_baseStation_parameter_updates){
      // We listen for new parameters
      LORA.receiveInstructions();

      // Then we listen for which measurements to add back to memory from 
      // SD card - TBD
      //LORA.receiveDesiredMeasrements();
      //sd_writer.fetchRequestedMeasurements(LORA.measurementTargets);
    }
    LORA.updateMeasurementFrequency(gps_manager.current_buoy_velocity, maximal_measurement_period, minimal_measurement_period);

  }
  
  sd_writer.logString("Transmission done");
  sd_writer.closeLog();

  sleep_cycles_transmission = 0;
  measurement_timer = millis();
  LORA.lastTransmission = millis();
  LORA.sleep();

}

void task_beacon(){
    LORA.wakeUp();
    gps_manager.updateBeaconMsg(LORA.WiO_ID);
    LORA.transmitBeaconMessage(gps_manager.beaconMsg, beaconMsgSize);
    sleep_cycles_beacon = 0;
    beacon_timer        = millis();
    LORA.sleep();
}

void loop() {
  /*
    We start by checking if we should switch on each sensor
  */
  IWatchdog.reload();
  bool disable_sensors = false;

  if (debug_serial){
    Serial.begin(serial_baud);
    delay(100);
    Serial.println("Booting up!");

  }

  // Measurement loop (temperature and GPS)
  if (millis_time_corrected(sleep_cycles_measurement) - measurement_timer > LORA.measurement_period){
      task_measure_gps_temp();
  }
  
  // Transmission protocol
  if ((millis_time_corrected(sleep_cycles_transmission) - LORA.lastTransmission > minimal_transmission_period) && 
      (gps_manager.GPSReadings.size() > packet_count_send_treshold)) {  
        task_transmit();
  }

  // Recovery protocol
  if ((millis_time_corrected(sleep_cycles_beacon) - beacon_timer > beacon_ping_period) && (enable_recovery_beacon)){
    task_beacon();
  }

  if (debug_serial){
    Serial.println("\n Succesfull iteration, starting to log\n");
    Serial.println("Logging finished");
    Serial.println(F("Shutting down"));
    delay(100);
    Serial.end();
  }
  
  // We sleep for "sleep_time" before waking up to refresh the watchdog
  IWatchdog.reload();
  sleep_cycles_measurement++;
  sleep_cycles_transmission++;
  if (sd_writer.active){
    sd_writer.shutdown();
  }
  delay(150);
  LowPower.sleep(sleep_time);
}

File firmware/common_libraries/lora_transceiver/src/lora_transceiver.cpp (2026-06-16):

#include "lora_transceiver.h"


LoRa_Transceiver LORA;

void setFlag(void){
  // Function called by RadioLib to mark completed operation
  operationDone = true;
}


// Read Buoy ID from wio device
void LoRa_Transceiver::getWiOID(void){
  // Only UID0 seems to be necessary 
  WiO_ID = HAL_GetUIDw0();
  if (debug_serial){
    Serial.print("Buoy ID: ");
    Serial.print(WiO_ID);
  }
}


void LoRa_Transceiver::computeReceptionChannel(uint8_t num_LoRa_channels, double fmin, double fmax){
  if (LoRa_freq_receive < 0){
    if (WiO_ID ==  0)
      getWiOID(); //In case we forgot to aquire ID
    
    // We use the modulo operator to get a "random" channel number
    uint8_t channelNo = WiO_ID % num_LoRa_channels;

    // We partition the domain into num_LoRa_channels equidistant channels, and choose the appropriate one
    LoRa_freq_receive = fmin + (fmax - fmin)*( (float) channelNo)/num_LoRa_channels;
  }
}


void LoRa_Transceiver::beginRadio(double freq, double bw, int sf, int cr, int power){
  /*
    Method to be called once, here we set the transmission parameters
    and set the appropriate flags. If you need to restart the radio
    use the changeFrequency method.
  */
  radio.setRfSwitchTable(rfswitch_pins, rfswitch_table);
  state = radio.begin(freq, bw, sf, cr, (0x12),power, 8,1.7, false);
  radio.setTCXO(1.7);
  radio.setDio1Action(setFlag);
  packet_count = 0;
  listening = false;
  delay(200);
  IWatchdog.reload();
}


/*
  Three message sending method
  the two former are for sending strings
  The latter for sending byte arrays.
  We recommend transmitting byte arrays 
  for efficiency
*/

void LoRa_Transceiver::transmit(String msg){
  transmit(msg.c_str());
}

void LoRa_Transceiver::transmit(const char * msg){
  if (debug_serial){
    Serial.println(msg);
  }
  radio.startTransmit(msg);
}


void LoRa_Transceiver::transmitB(byte * msg, uint8_t msgSize){
  radio.startTransmit(msg, msgSize);
}


float LoRa_Transceiver::getRSSI()
{
  return radio.getRSSI();
}

// Method called after the end of transmission to send the updated parameters
void LoRa_Transceiver::sendFinalMessage(FrequencyMessage frequency_message)
{
  create_update_message(frequency_message);
  sd_writer.debugSerialPrint("Sending end message ");
  sd_writer.debugByteArray(end_message, end_message_size);
  sd_writer.debugSerialPrintln("");

  changeFrequency(send_frequency);
  radio.startTransmit(end_message, end_message_size);
  msgCounter++;
}


void LoRa_Transceiver::changeFrequency(double f){
  /*
    This method restarts the radio with a new given frequency. 
  */
  state = radio.begin(f, LoRa_bw, LoRa_sf, LoRa_cr, (0x12), LoRa_power, 8,1.7, false);
  radio.setTCXO(1.7);
  radio.setDio1Action(setFlag);
  listening = false;
  delay(200);
  IWatchdog.reload();

   if (debug_serial){
    Serial.print("Radio restarted at frequency: ");
    Serial.println(f);
  }
}

void LoRa_Transceiver::setDefaultSendFrequency(double freq){
  send_frequency = freq;
}

void LoRa_Transceiver::setBaseStationID(uint8_t id){
  baseStationID = id;
}
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

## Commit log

2025-12-19 Buoy PCB added
    [OLB-B_Cu.gbl, OLB-B_Mask.gbs, OLB-B_Paste.gbp, OLB-B_Silkscreen.gbo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]
2025-12-19 BST PCB
    [BST_BCP.stl, BST_BCP_v2.stl, BST_PCB-B_Cu.gbr, BST_PCB-B_Mask.gbr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]
2026-03-17 read GPS example fixed, removed redundant dependency. Added in OneWire by Paul Stofregen to the Thermo manager for compatability
    [moored_PCB.kicad_pcb, moored_PCB.kicad_sch]
2026-06-10 Extra debug prints
2026-06-10 Removed unecessary debug print
2026-06-16 Merging into pull request
    [BST_PCB-B_Cu.gbr, BST_PCB-B_Mask.gbr, BST_PCB-B_Paste.gbr, BST_PCB-B_Silkscreen.gbr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]
2026-06-22 Change resistor value in README
    Updated resistor specification from 1.0 kOhm to 10 kOhm.
2026-06-22 Fixed schematic bugs
    [BST_PCB.kicad_sch, OLB.kicad_sch]
2026-06-22 Added more documentation, fixed BST PCB
    [BST_PCB.kicad_pcb]
2026-06-25 Fix battery holder type and typos in README
    Corrected battery holder type for Adafruit Ultimate GPS and fixed minor typos throughout the document.
